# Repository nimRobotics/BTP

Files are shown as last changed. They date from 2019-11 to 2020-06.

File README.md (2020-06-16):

# :warning: [Deprecated for public use]

Please check <https://nimrobotics.github.io/OpenKDM/>.

# Introduction

This work titled as "Design and Fabrication of Experiment for Dynamic Analysis of Mechanisms " has been undertaken jointly by [Aakash Yadav](http://nimrobotics.github.io/) and Akhil Akunuru under the guidance of [Prof. Sriram Sundar](https://iittp.ac.in/dr-sriram-sundar).

|website| GitHub |
|--|--|
| [https://nimrobotics.github.io/BTP/](https://nimrobotics.github.io/BTP/) | [https://github.com/nimRobotics/BTP](https://github.com/nimRobotics/BTP) |

## Motivation and objective

The study of the *"Kinematics and Dynamics of Machinery" (IITT course code: ME2206)* lies at the very core of a mechanical engineering
background. Although, little has changed in the way the subject is presented, our methodology brings the subject alive and current. We
present the design and fabrication of a novel experimental setup for carrying out static, kinematic and dynamic analysis of three different
mechanisms in a single setup (Figure <a href="#cad_ful" data-reference-type="ref" data-reference="cad_ful">1</a>). The mechanism is designed to be configurable to three different types of mechanisms namely - double crank, slider crank and a six bar mechanism depending on the use case as shown in Figure <a href="#cad_all" data-reference-type="ref" data-reference="cad_all">2</a>. The mechanism has retrofitted parts (different link lengths and sliders) to facilitate multiple experiments in the same setup.

The learner gets to "play" with the mechanism parameters and immediately understand their effects. This will enhance one’s grasp of the concepts
and the development of analytical skills. Hence greatly supplementing and reinforcing the theoretical understanding of the undergraduate
students taking the course.

<figure align="center">
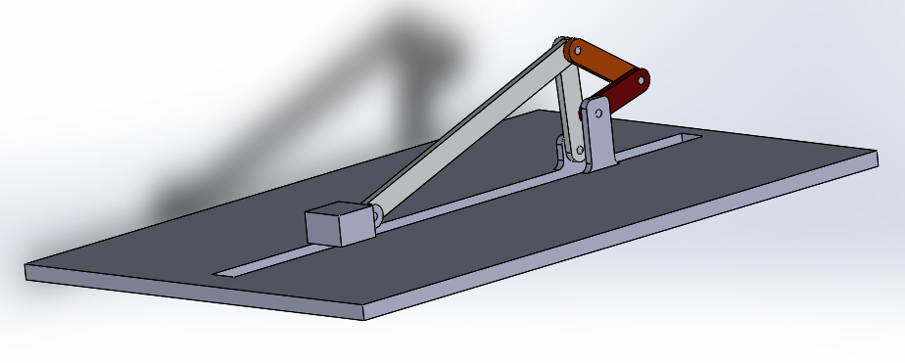
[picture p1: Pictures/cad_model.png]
<figcaption>1. CAD model of the mechanism</figcaption>
</figure>

<figure align="center">
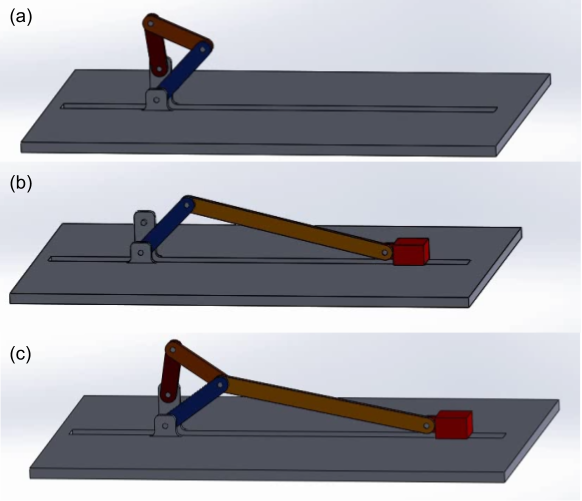
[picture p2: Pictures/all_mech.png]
<figcaption>2. Three possible configurations of the mechanism: (a) Four bar, (b) Slider crank and (c) Six bar</figcaption>
</figure>

## Present method(s) and challenges

In the present scenario finding standard mechanisms integrated with different sensor measurements and data acquisition is hard to find.
Almost all the mechanisms that are available off-the-shelf do not have any data measurement capability and thus can only be used for
demonstrations purpose and not as an experimental setup. 

In chapter 2 we present thoroughly all the methodologies used in designing and modeling the mechanisms. This includes both the analysis
carried out by analytical as well as numerical methods. In the chapter that follows we bring out the various design considerations that have to
be taken into account while manufacturing the product. The final two sections present the result(s) and the conclusion(s).

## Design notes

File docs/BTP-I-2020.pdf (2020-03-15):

## Department of Mechanical Engineering Indian Institute of Technology Tirupati

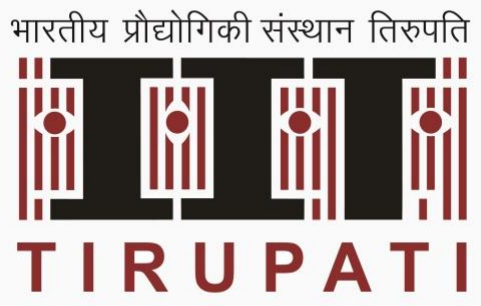
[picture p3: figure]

# B. Tech Final Year Project Presentation

## DESIGN AND FABRICATION OF EXPERIMENT FOR DYNAMIC ANALYSIS OF MECHANISMS

### 1. Aakash (ME16B001) 2. A. Akhil (ME16B003)

Supervised by
1. Dr. Sriram Sundar, Assistant Prof of ME

Date: 11-Mar-2020

## Objectives and Motivation

Dept. of
Mechanical
Engineering
B. Tech Final
Year Project
Presentation
- Introduction - Design and fabrication of experimental setup for static, kinematic and dynamic analysis of mechanisms with retrofitted parts.
- Motivation - The experiment will supplement and reinforce the theoretical understanding of the undergraduate students taking the ME2206 (KDM) course.

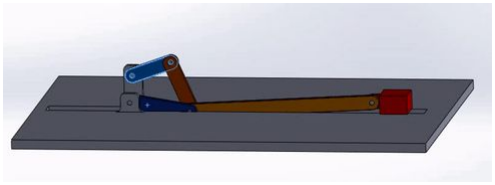
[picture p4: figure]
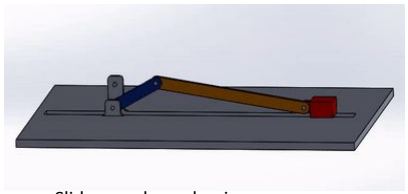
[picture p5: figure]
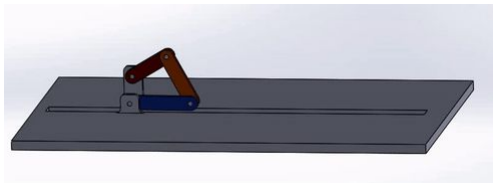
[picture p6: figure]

Four bar mechanism | Slider crank mechanism

Six bar mechanism

## Experiment plan

Aim:
1. To find the slider velocity and acceleration for six bar mechanism and slider crank mechanism
2. To find angular velocity and angular acceleration of all links in double crank mechanism.

Methodology and Results:
- This experimental setup will store the data of all parameters for each angular position.
- Students can select the angular position in the experimental setup to get the stored data display.
- Students need to solve theoretically for any particular angular position of mechanism.
- Students can compare theoretical results with practical results.

Engineering
Presentation

## Manufacturing plan

Engineering
Presentation

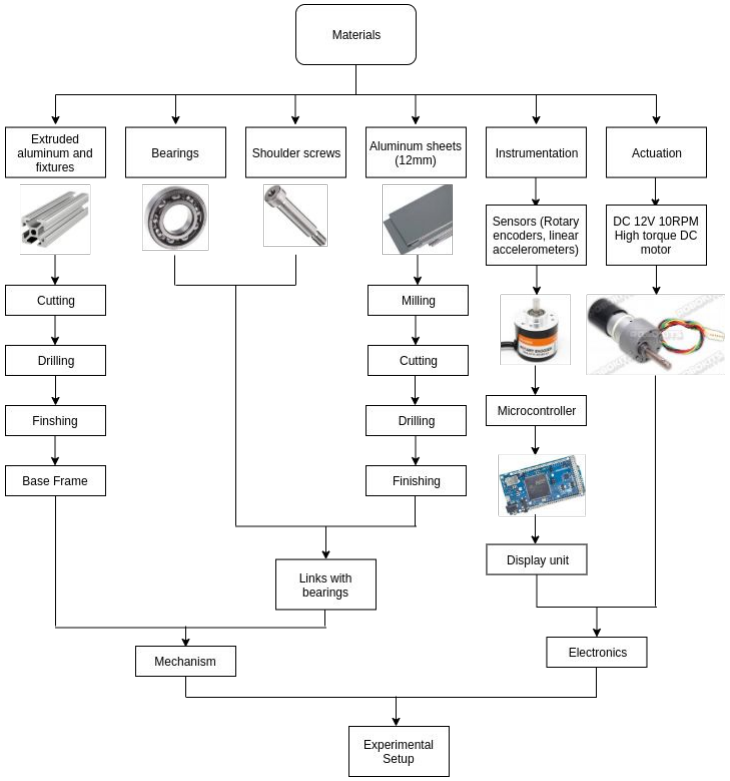
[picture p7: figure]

Sources: Bearing(SKF), Extruded Aluminum(indiamart.com), Shoulder screw(indiamart.com), AL sheets (indiamart.com)

## Updated CAD Design

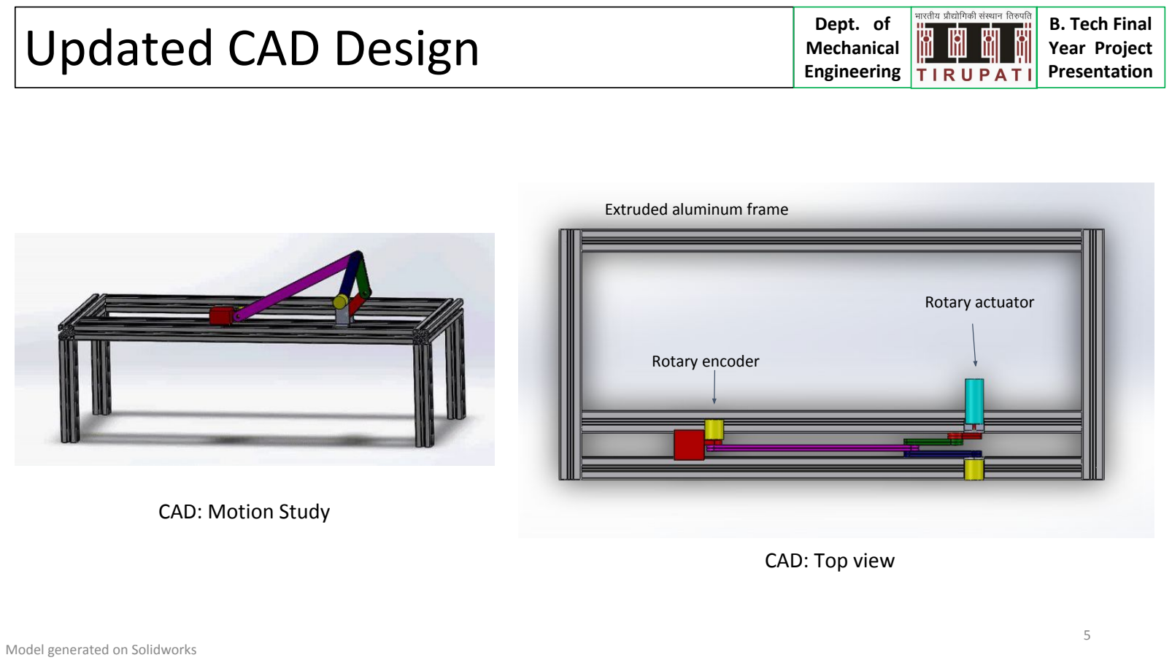
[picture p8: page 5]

Engineering
Presentation

CAD: Motion Study

CAD: Top view

Rotary actuator

Extruded aluminum frame

Rotary encoder

Model generated on Solidworks

## Raw materials

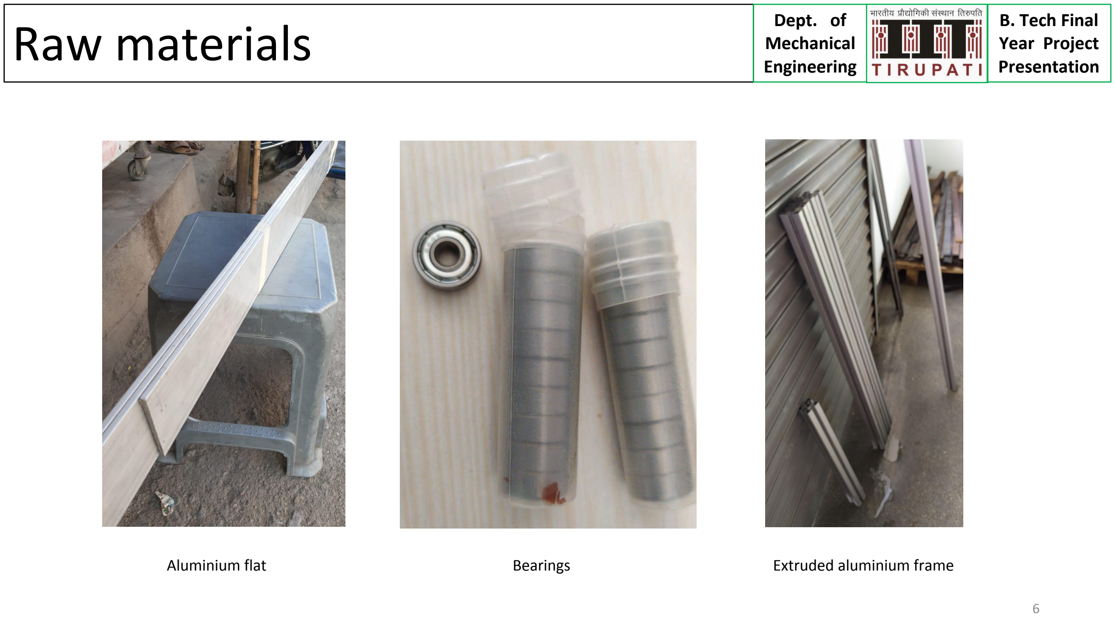
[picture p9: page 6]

Engineering
Presentation
Aluminium flat | Bearings | Extruded aluminium frame

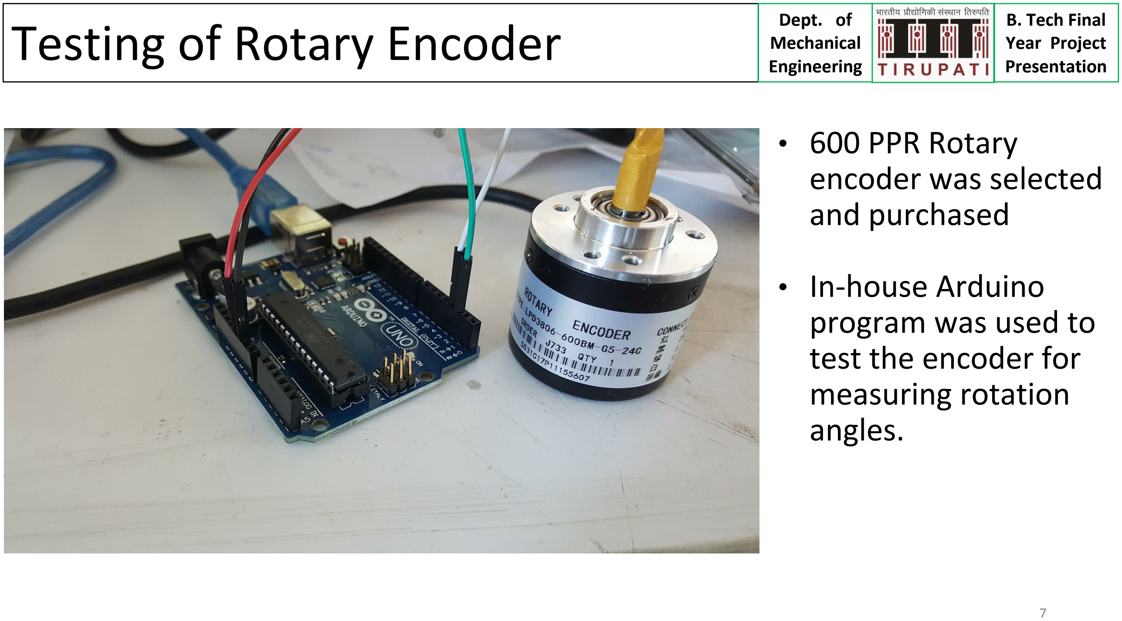
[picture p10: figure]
Testing of Rotary Encoder; Engineering; Presentation; • 600 PPR Rotary encoder was selected and purchased; • In-house Arduino program was used to test the encoder for measuring rotation angles.

## Actuator selection

Engineering
Presentation

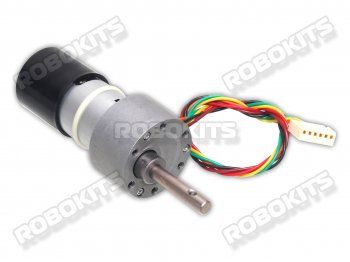
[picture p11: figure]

DC 12V 10 rpm high torque
quad encoder motor

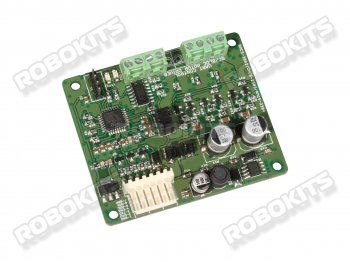
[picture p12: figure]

DC servo driver

Image source: Robokits India

## Fabrication

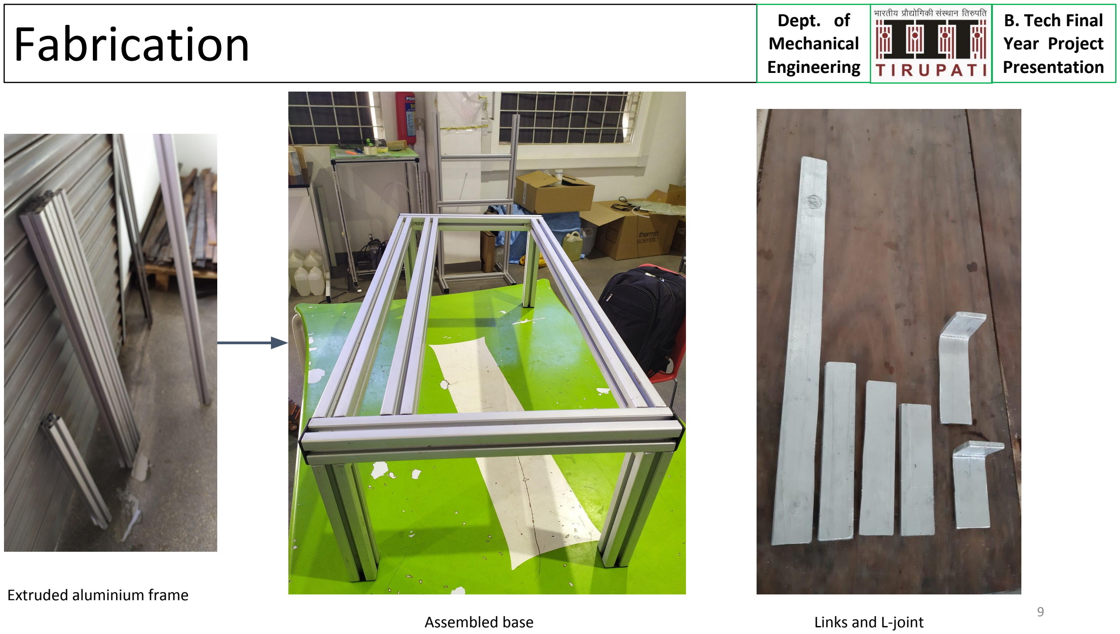
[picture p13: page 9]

Engineering
Presentation

Extruded aluminium frame

Assembled base | Links and L-joint

## Conclusions

- Full fledged CAD model of the mechanism was created considering all the manufacturing challenges (Design for manufacturing).
- All the required raw material were procured
- Rotary encoders were tested for angle measurement using Arduino.
- The base frame has been assembled while manufacturing and assembly of the links is in process.

Engineering
Presentation

## Future Work

Engineering
Presentation

Documentation

- Creation of
experiment
manual and
documentation.

Testing
(10th April)
- Experimentation,
testing and
validation.
- Design changes if
required

Fabrication
(31st March)
- Fabrication and
assembly of
links.
- Integration of
encoders and
other
electronics

## References

1. A. Ghosh and A. K. Mallik, Theory of mechanisms and machines. Affiliated East-West Press Private Limited, 2002.
2. R. L. Norton, Kinematics and dynamics of machinery. McGraw-Hill Higher Education, 2011.
3. J. J. Uicker, G. R. Pennock, J. E. Shigley, et al., Theory of machines and mechanisms, volume 1. Oxford University Press New York, NY, 2011.

Engineering
Presentation

## END

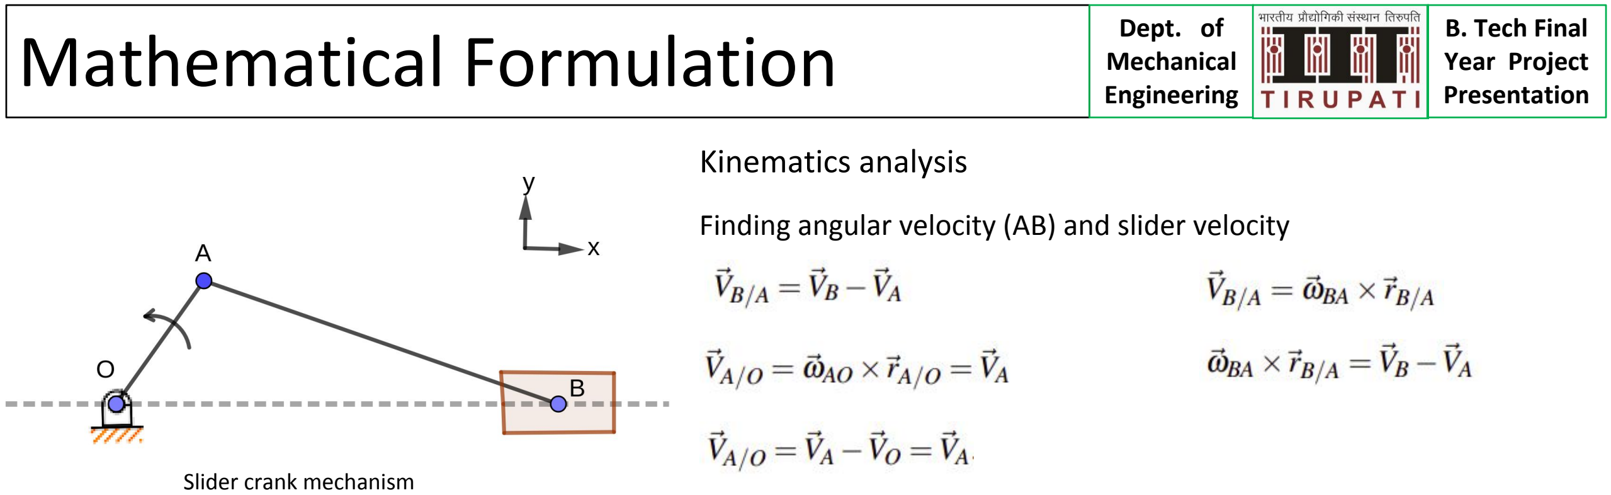
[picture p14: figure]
Mathematical Formulation; Engineering; Presentation; Kinematics analysis; Slider crank mechanism

Note: there may be missing steps and common notations for the sake of brevity. Refer to report for completeness.

Finding angular velocity (AB) and slider velocity

Finding angular acceleration (AB) and slider acceleration

## Mathematical Formulation

Engineering
Presentation

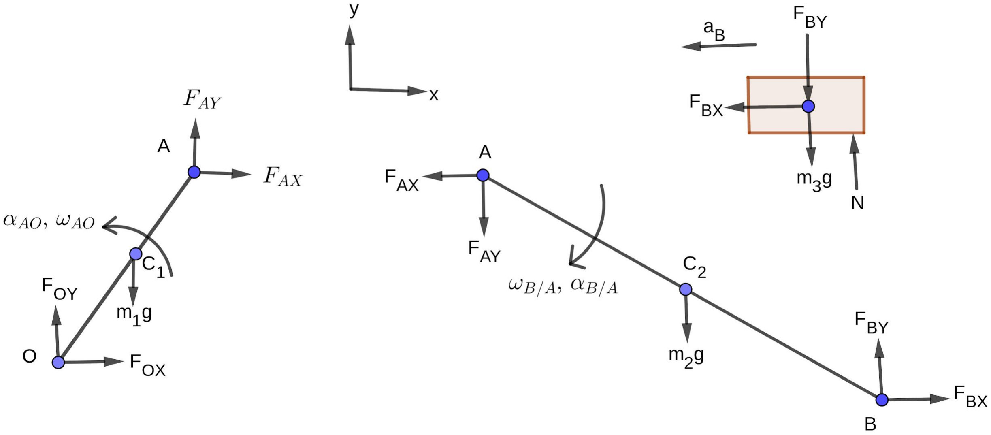
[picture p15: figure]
Slider crank mechanism

Dynamic analysis

Note: there may be missing steps and common notations for the sake of brevity. Refer to report for completeness.

Force balance for slider

Force and torque balance for link OA

Force and torque balance for link AB

Kinematic Analysis | Dept. of Engineering

Presentation
- By using Geogebra, we obtained preliminary link lengths and slider velocity profile.
- Analysed the velocity profile by changing link lengths.

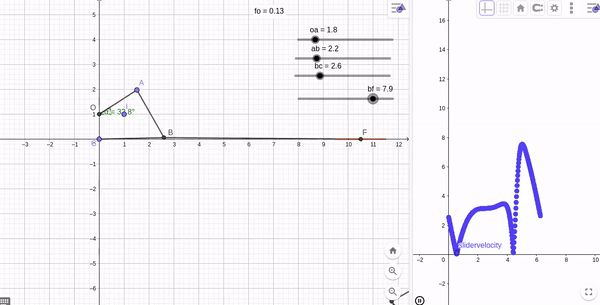
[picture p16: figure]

## Design for constant velocity

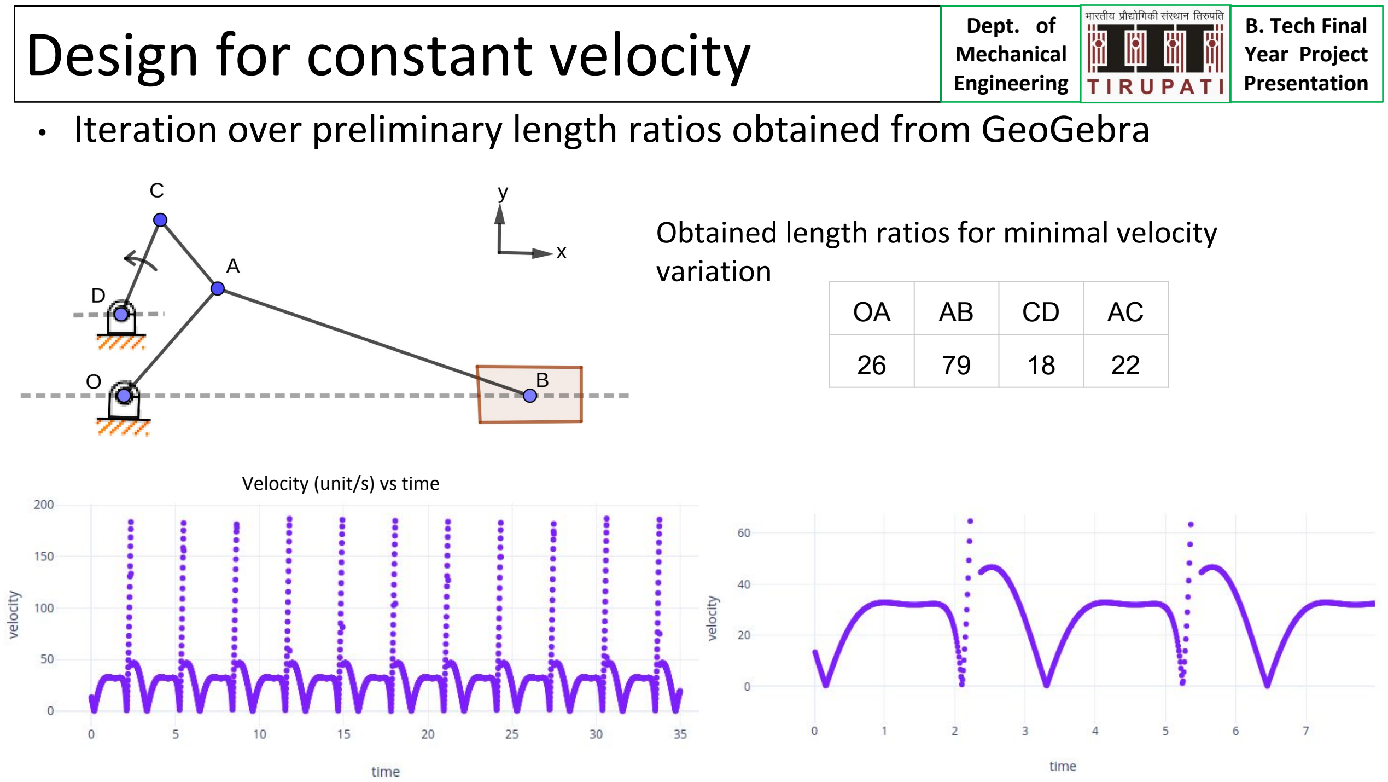
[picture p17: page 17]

- Iteration over preliminary length ratios obtained from GeoGebra

Engineering
Presentation
OA | AB | CD | AC
26 | 79 | 18 | 22

Obtained length ratios for minimal velocity variation

Velocity (unit/s) vs time

Dynamic Analysis | Dept. of

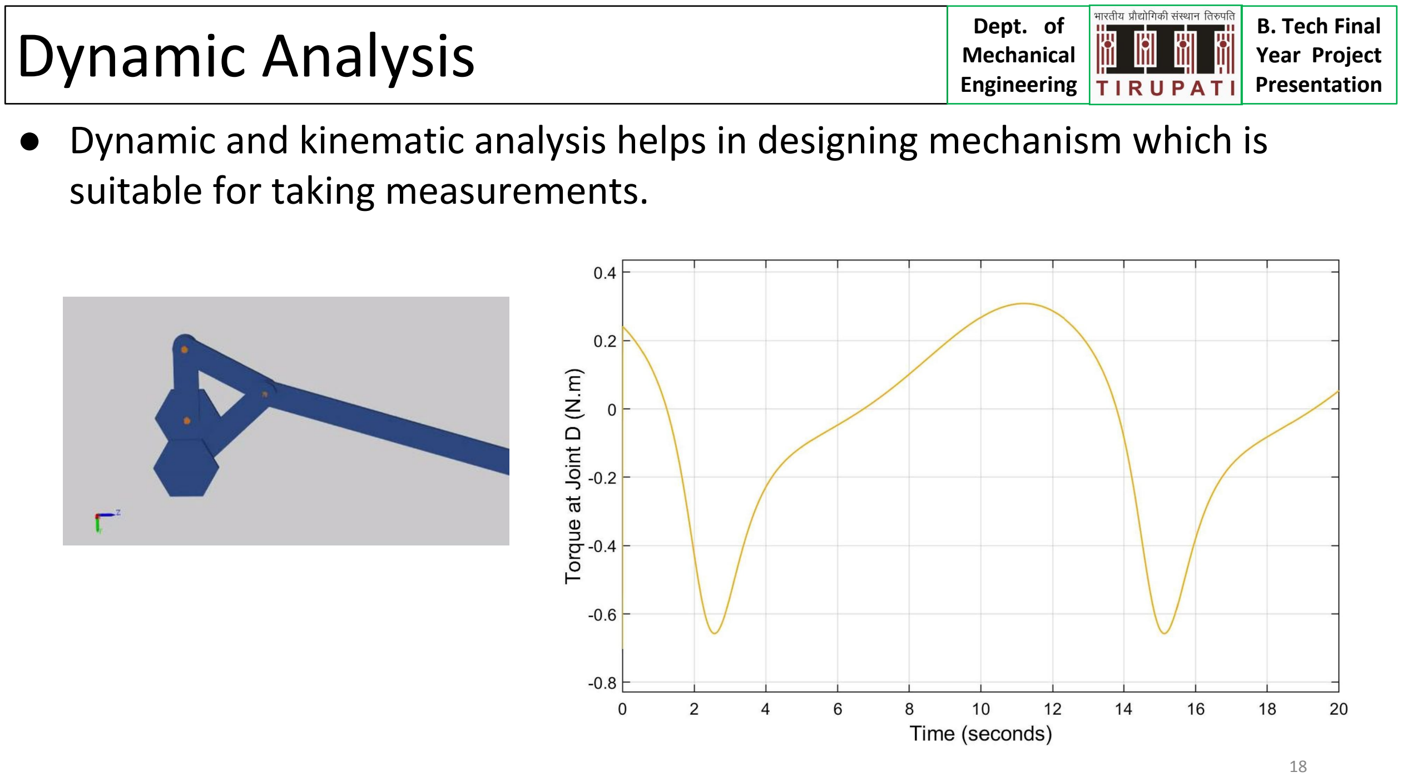
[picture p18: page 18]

Engineering
Presentation
- Dynamic and kinematic analysis helps in designing mechanism which is suitable for taking measurements.

## Results

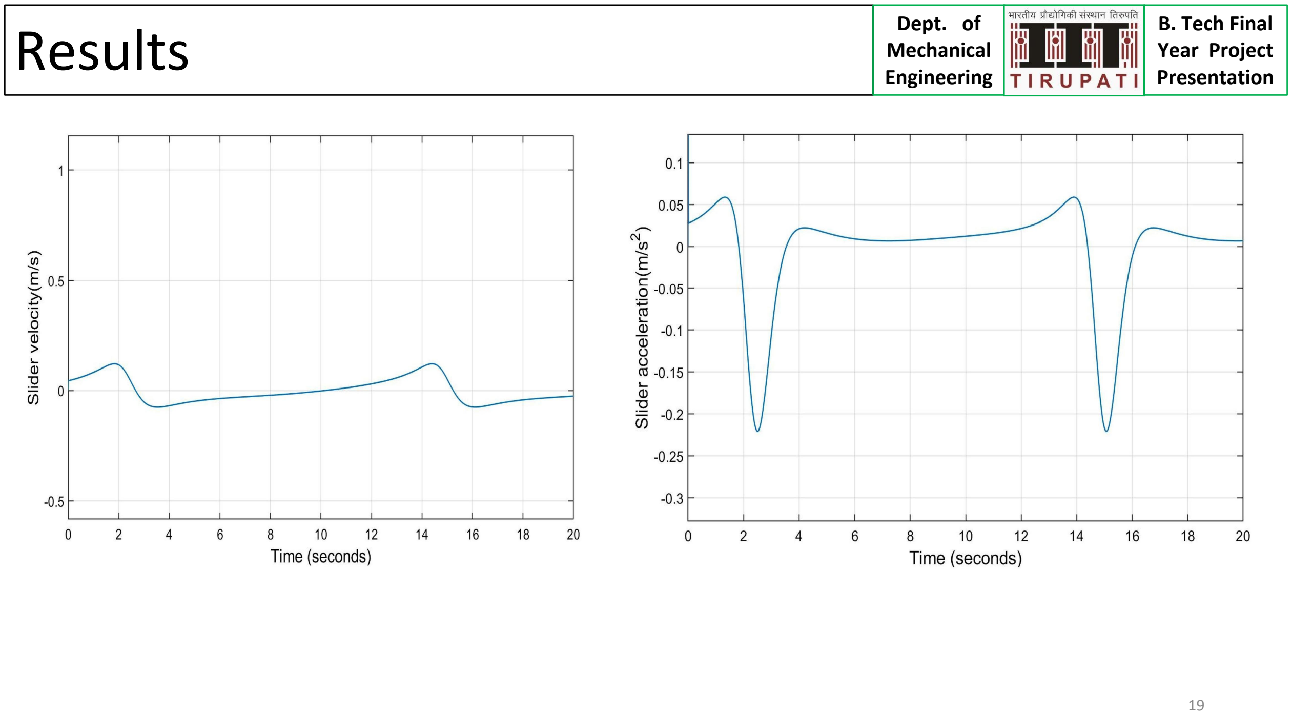
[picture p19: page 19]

Engineering
Presentation

## 3D Model

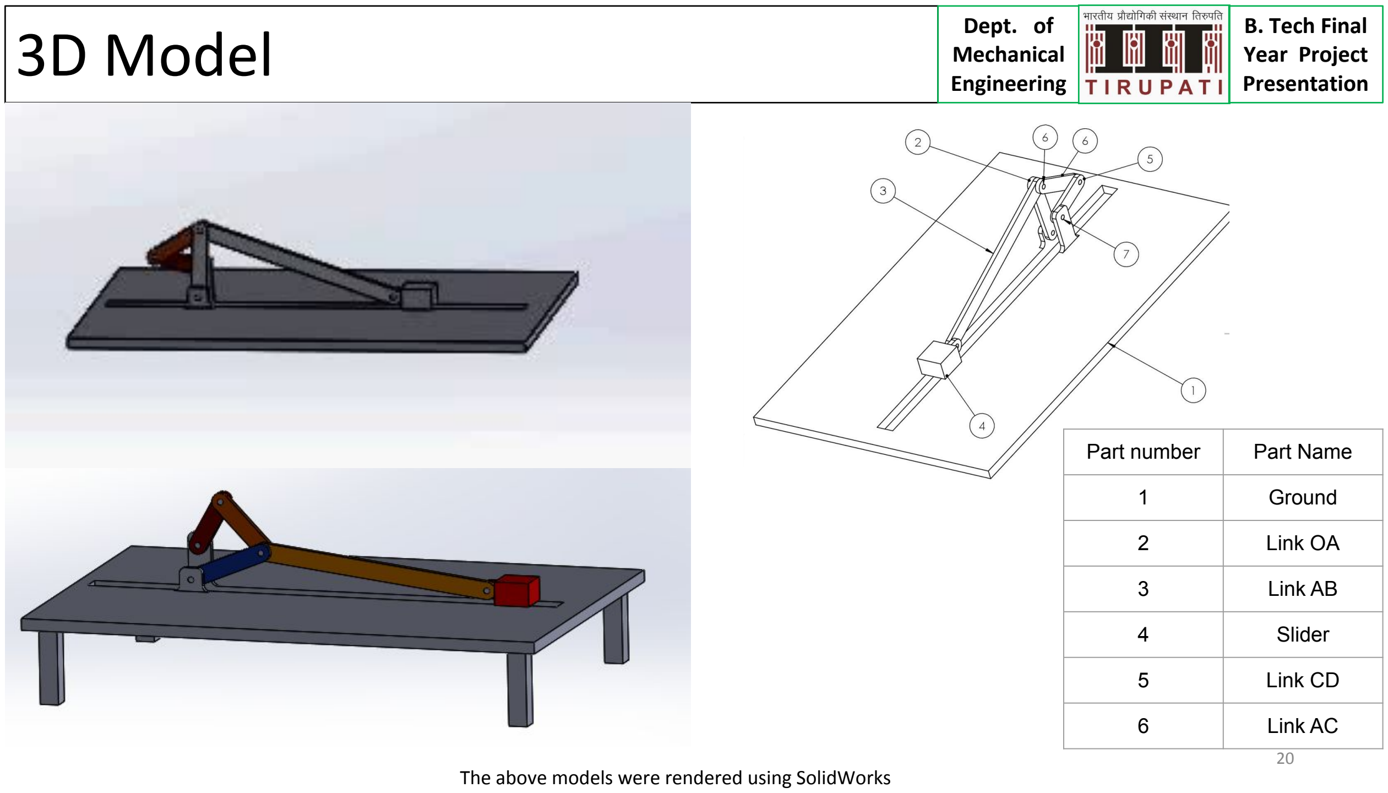
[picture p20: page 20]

Engineering
Presentation
Part number | Part Name
1 | Ground
2 | Link OA
3 | Link AB
4 | Slider
5 | Link CD
6 | Link AC

The above models were rendered using SolidWorks

## Sensor selection

Based on the results obtained from kinematic and dynamic analysis using MathWorks Simscape, we selected the required sensors.

- 2-Phase Incremental Optical Rotary Encoder to detect angular velocity and angular acceleration of links
- 3-Axis Accelerometer is to detect linear acceleration and linear velocity of slider.

Engineering
Presentation

Source: robu.in

Source: amazon.in

## Cost Analysis

Engineering
Presentation
No | Name | Unit cost in INR | Quantity | Cost in INR
1 | Bearing | 50 | 20 | 1000
2 | Shoulder screw | 20 | 6 | 120
3 | Aluminum (for links and slider) | 200 per kg | 15kg | 3000
4 | Extruded Aluminum | 400 per m | 5 | 2000
5 | Actuator | - | - | -
6 | Rotary Encoder | 2000 | 3 | 6000
7 | Linear Accelerometer (8kHz) | 200 | 1 | 200
8 | Display | 1000 | 1 | 1000
9 | Other Electronics and miscellaneous | | | 5000
10 | Slotted weights, pulley | 2000 | 1 | 2000
| Grand Total | | | 20,320/-

Note: tentative, minor changes may occur.

## Conclusions

- The complete analysis of the mechanism(s) was performed using applicable method and software.
- 3D CAD model of the mechanism was created to facilitate better visualisation.
- Various design considerations were addressed and manufacturing workflow and plan were accomplished as a prerequisite to manufacturing.
- BoM was prepared and materials acquisition from the vendor is in process.

Engineering
Presentation

## Future Work

Engineering
Presentation

Fabrication

- Fabrication and
assembling of
links.
- Experimentation,
testing and
validation.

Final Design

- Final prototype
model consisting
of links, bearings,
motors, sensors,
etc.

Actuator selection

- Need to find the
best actuator
with its control
system.

## References

1. MATLAB version 9.3.0.713579 (R2017b). The Mathworks, Inc., Natick, Massachusetts, 2017.
2. A. Ghosh and A. K. Mallik, Theory of mechanisms and machines. Affiliated East-West Press Private Limited, 2002.
3. M. Hohenwarter, M. Borcherds, G. Ancsin, B. Bencze, M. Blossier, A. Delobelle, C. Denizet, J. Éliás, A. Fekete, L. Gál, Z. Konecný ˇ , Z. Kovács, S. Lizelfelner, B. Parisse, and G. Sturr (2013). GeoGebra 4.4. http://www.geogebra.org.
4. R. L. Norton, Kinematics and dynamics of machinery. McGraw-Hill Higher Education, 2011.
5. Python Core Team (2018). Python: A dynamic, open source programming language. Python Software Foundation. URL https://www.python.org/.
6. J. J. Uicker, G. R. Pennock, J. E. Shigley, et al., Theory of machines and mechanisms, volume 1. Oxford University Press New York, NY, 2011.

Engineering
Presentation

## Acknowledgements

Thanks to all those who helped us during the course of our B.Tech. project at IIT Tirupati. We are thankful to and fortunate enough to get constant encouragement, support and guidance from Dr. Sriram Sundar of Mechanical Engineering Department which helped us in successfully completing first phase of our project work. We would also like to extend our sincere esteems to all staff in laboratory for their timely support.

To our families, thank you for encouraging us in all of our pursuits and inspiring us to follow our dreams. We are especially grateful to our parents, who supported us emotionally and financially.

Engineering
Presentation

## END

## Supplementary material

## Updates

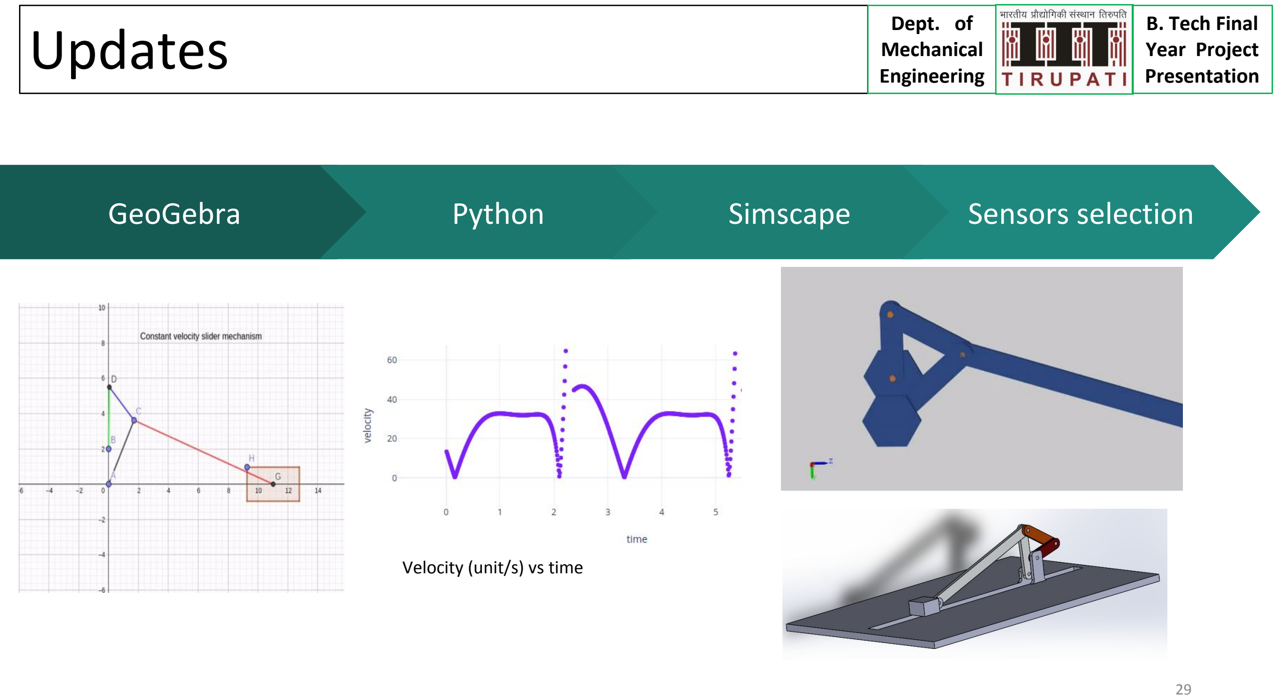
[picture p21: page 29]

Engineering
Presentation
GeoGebra | Python | Simscape | Sensors selection

Velocity (unit/s) vs time

## Introduction and Objectives

- To design and fabricate an experimental setup for static, kinematic and dynamic analysis of mechanism.
- The setup will have retrofitted parts in order to let the student carry out multiple experiments in the same setup.
- The experiment will supplement and reinforce the theoretical understanding of the undergraduate students taking the ME2206(KDM) by providing them the opportunity to match the analytical results with the actual experimental results.

Engineering
Presentation

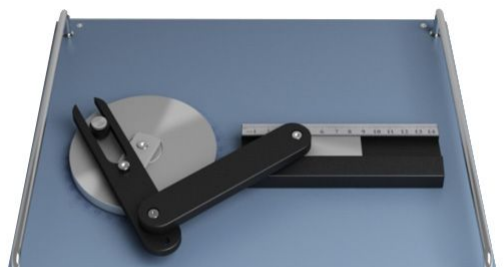
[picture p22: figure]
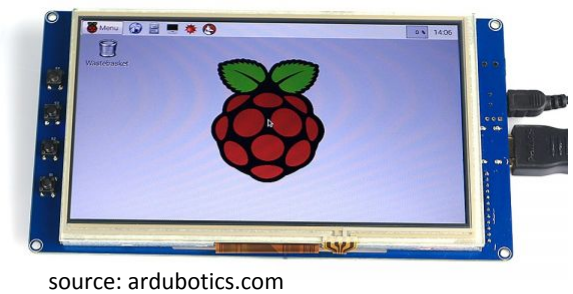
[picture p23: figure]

source: sun labtech source: ardubotics.com

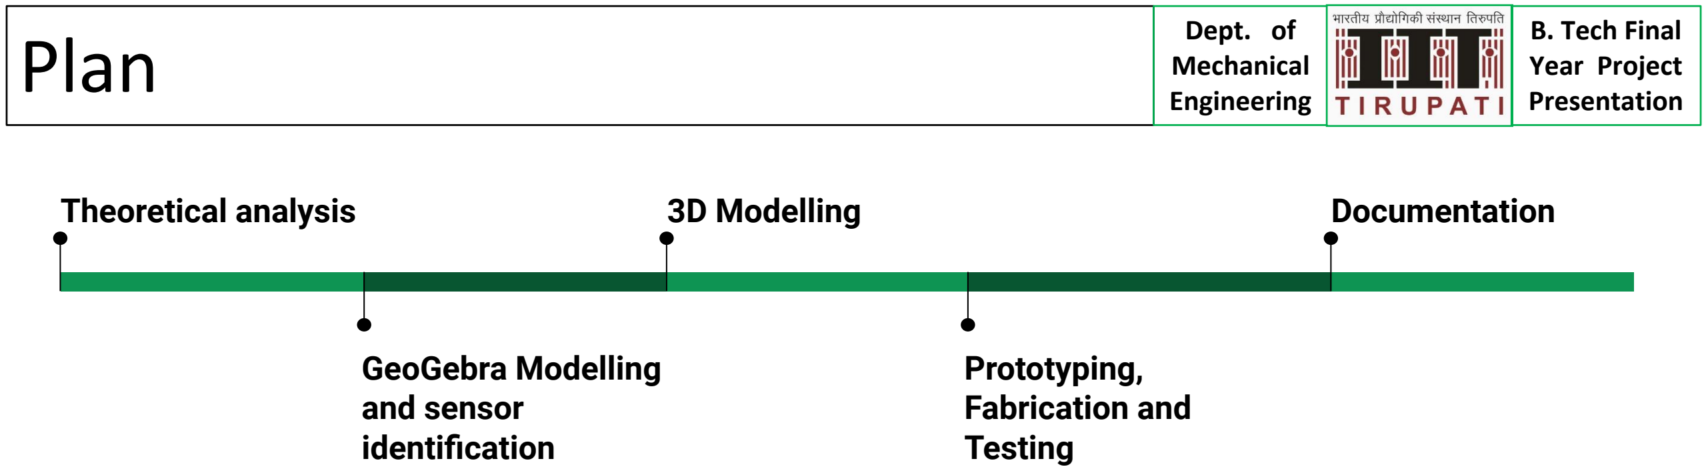
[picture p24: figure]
Plan; Engineering; Presentation; 3D Modelling; Prototyping, Fabrication and Testing; Theoretical analysis; GeoGebra Modelling and sensor identification; Documentation

Estimated budget : INR 25,000.00 - 30,000.00

Probable sensors for instrumentation: Rotary encoders, Ultrasonic range sensors, linear accelerometers, strain gauges

## Literature Review

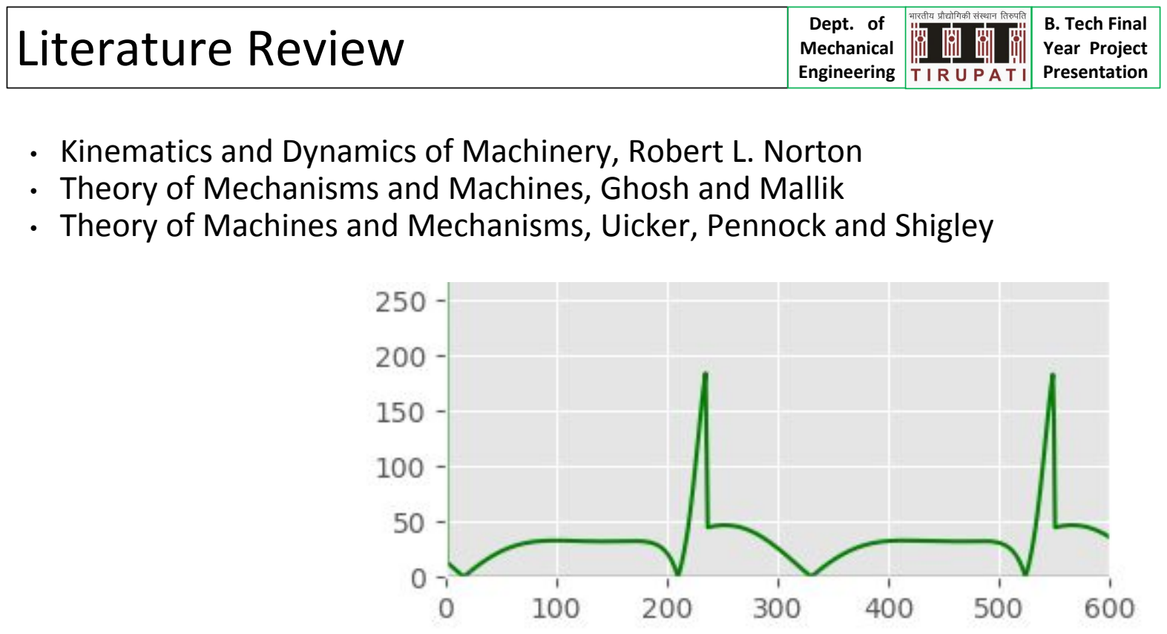
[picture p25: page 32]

- Kinematics and Dynamics of Machinery, Robert L. Norton
- Theory of Mechanisms and Machines, Ghosh and Mallik
- Theory of Machines and Mechanisms, Uicker, Pennock and Shigley

Engineering
Presentation

## Mechanism

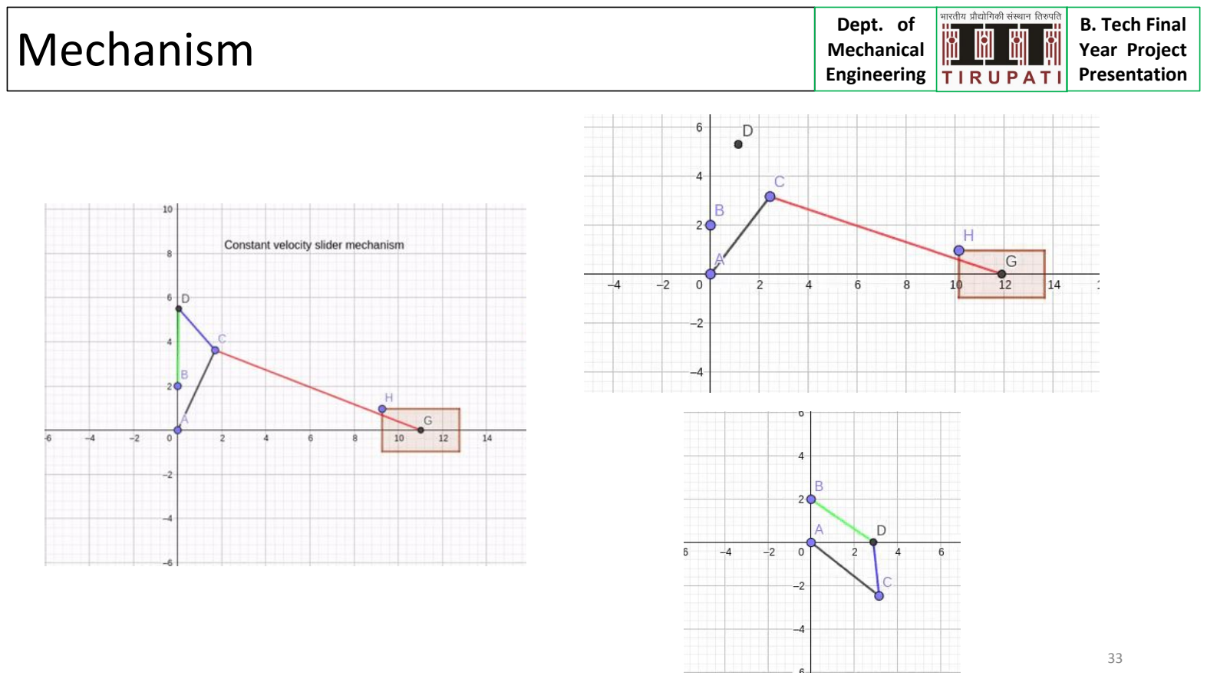
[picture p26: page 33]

Engineering
Presentation

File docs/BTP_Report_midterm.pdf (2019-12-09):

## Design and Fabrication of Experiment for Dynamic

## Analysis of Mechanisms

submitted in partial fulfilment of the requirements

for the degree of

BACHELOR OF TECHNOLOGY

in

MECHANICAL ENGINEERING

by

### AAKASH ME16B001

### A. AKHIL ME16B003

### Supervisor(s)

### Dr. Sriram Sundar

### DEPARTMENT OF MECHANICAL ENGINEERING

### INDIAN INSTITUTE OF TECHNOLOGY TIRUPATI

### December 2019

## DECLARATION

We declare that this written submission represents our ideas in our own words

and where others’ ideas or words have been included, we have adequately cited and

referenced the original sources. We also declare that we have adhered to all principles of

academic honesty and integrity and have not misrepresented or fabricated or falsified any

idea/data/fact/source in our submission. We understand that any violation of the above

will be cause for disciplinary action by the Institute and can also evoke penal action from

the sources which have thus not been properly cited or from whom proper permission

has not been taken when needed.

Place: Tirupati
Date: 06-12-2019

Signature
Aakash
ME16B001

Place: Tirupati
Date: 06-12-2019

Signature
A. Akhil
ME16B003

## BONA FIDE CERTIFICATE

This is to certify that the thesis titled Design and Fabrication of Experiment for

Dynamic Analysis of Mechanisms, submitted by Aakash and A. Akhil, to the Indian

Institute of Technology, Tirupati, for the award of the degree of Bachelor of Technology,

is a bona fide record of the research work done by them under my supervision. The

contents of this thesis, in full or in parts, have not been submitted to any other Institute

or University for the award of any degree or diploma.

Place: Tirupati
Date: 08-12-2019

Dr. Sriram Sundar
Guide
Assistant Professor
Department of Mechanical
Engineering
IIT Tirupati - 517501

## ACKNOWLEDGEMENTS

Thanks to all those who helped us during the course of our B.Tech. project at IIT Tirupati.

We are thankful to and fortunate enough to get constant encouragement, support and

guidance from Dr. Sriram Sundar of Mechanical Engineering Department which helped

us in successfully completing first phase of our project work. We would also like to

extend our sincere esteems to all staff in laboratory for their timely support.

To our families, thank you for encouraging us in all of our pursuits and inspiring us

to follow our dreams. We are especially grateful to our parents, who supported us

emotionally and financially.

i

## ABSTRACT

KEYWORDS: Slider crank mechanism; Four bar mechanism; Six-bar mechanism;

Dynamic analysis; Kinematic analysis; Simulation.

This report explains the detailed process of design and analysis of an experimental

setup, which consists of a 3-in-1 mechanism. The setup is designed to perform static,

kinematic and dynamic analysis of mechanisms. The design and analysis were performed

analytically and numerically by using various commercial software’s. The results thus

obtained were used to determine the link geometry of the mechanism and in selecting

the suitable sensors which in turn will be used for fabrication and instrumentation.

ii

## TABLE OF CONTENTS

ACKNOWLEDGEMENTS | i
ABSTRACT | ii
LIST OF FIGURES | v
LIST OF TABLES | vi
ABBREVIATIONS | vii
NOTATION | viii
1 INTRODUCTION | 1
2 ANALYSIS OF MECHANISMS | 3
3 MANUFACTURING | 15
4 RESULTS | 17
5 CONCLUSION AND FUTURE WORK | 19

iii

A CODE LISTING | 20

## LIST OF FIGURES

1.1 CAD model of the mechanism | | 1

1.2 Three possible configurations of the mechanism: (a) Four bar, (b) Slider
crank and (c) Six bar | | 2
2.1 Slider crank mechanism | | 4
2.2 Four bar mechanism | | 5
2.3 Six bar mechanism | | 6

2.4 Snapshot from GeoGebra showing the mechanism (left) and the velocity
profile (right) | | 8
2.5 Output window from Python for kinematic simulation | | 9
2.6 Free Body Diagram for Slider Crank Mechanism | | 10
2.7 Free Body Diagram for four-bar mechanism | | 12
2.8 Free Body Diagram for six-bar mechanism | | 13
2.9 CAD model in MATLAB Simscape | | 13
2.10 Results obtained from Simscape | | 14
3.1 3D Model of the experiment on (table) | | 15
3.2 Flowchart showing manufacturing | | 16
4.1 Slider Velocity | | 17
4.2 Slider acceleration | | 18

v

## LIST OF TABLES

2.1 GeoGebra results | | 9
4.1 Final link lengths | | 17

vi

## ABBREVIATIONS

The following list describes the significance of various abbreviations and acronyms used

throughout the report.

KDM | Kinematics and Dynamics of Machinery
PMSM | Permanent Magnet Synchronous Motor
CAD | Computer Aided Design
CSV | Comma Seperated Values
FBD | Free Body Diagram

vii

## NOTATION

The following notations are used throughout the report.

~rA/B | Position vector of point A with respect to point B, m
ωAB | Angular velocity of link AB, rad
| s
~VA/B | Velocity vector of point A with respect to point B, m
| s
~aA/B | Acceleration vector of point A with respect to point B,

m
s

2
αAB | Angular acceleration of link AB, rad
| s
| 2

viii

## CHAPTER 1

## INTRODUCTION

## 1.1 Motivation and objective

The study of the "Kinematics and Dynamics of Machinery" (IITT course code: ME2206)

lies at the very core of a mechanical engineering background. Although, little has

changed in the way the subject is presented, our methodology brings the subject alive and

current. We present the design and fabrication of a novel experimental setup for carrying

out static, kinematic and dynamic analysis of three different mechanisms in a single

setup (Figure 1.1). The mechanism is designed to be configurable to three different types

of mechanisms namely - double crank, slider crank and a six bar mechanism depending

on the use case as shown in Figure 1.2. The mechanism has retrofitted parts (different

link lengths and sliders) to facilitate multiple experiments in the same setup.

The learner gets to "play" with the mechanism parameters and immediately understand

their effects. This will enhance one’s grasp of the concepts and the development of ana-

lytical skills. Hence greatly supplementing and reinforcing the theoretical understanding

of the undergraduate students taking the course.


Figure 1.1: CAD model of the mechanism

## 1.2 Present method(s) and challenges

In the present scenario finding standard mechanisms integrated with different sensor

measurement and data acquisition is hard to find. Almost all the mechanisms that are


Figure 1.2: Three possible configurations of the mechanism: (a) Four bar, (b) Slider crank and (c) Six bar

available off-the-shelf do not have any data measurement capability and thus can only be

used for demonstrations purpose and not as an experimental setup.

In chapter 2 we present thoroughly all the methodologies used in designing and modelling

the mechanisms. This includes both the analysis carried out by analytical as well

as numerical methods. In the chapter that follows we bring out the various design

considerations that has to be taken into account while manufacturing the product. The

final two sections present the result(s) and the conclusion(s).

## CHAPTER 2

## ANALYSIS OF MECHANISMS

## 2.1 Kinematic analysis

This section presents the methodology employed in order to simulate the kinematics of

the various mechanisms. In order to carry out the preliminary analysis of the mechanism,

GeoGebra an interactive math and geometry software was used. This provided the coarse

link lengths required for having the least deviant constant velocity mechanism as shown

in Figure 2.4. Once the coarse link lengths were obtained, we developed an in-house

Python code that can do iterations on the link lengths so as to minimise any fluctuations

in the constant velocity mechanism. The visual output of the Python simulation can be

seen in Figure 2.5 while rest of the simulation data is store in a CSV file.

### 2.1.1 Mathematical formulation

This section brings out the equations of motion associated with the three different

mechanisms (Norton, 2011; Uicker et al., 2011). These equations are used to carry out

the kinematic and dynamics method theoretically, which then in turn be compared with

the numerical solutions obtained by other simulation tools.

Slider crank mechanism

The equations of motion pertaining to the slider crank mechanism (Figure 2.1) are

presented in this subsection.

~VB/A =~VB −~VA | (2.1)

For link OA we have

~VA/O = ω~ AO ×~rA/O =~VA | (2.2)


Figure 2.1: Slider crank mechanism

Since ’O’ is ground link we have ~VO = 0 =⇒ ~VA/O =~VA −~VO =~VA. As point B lies on

the slider and is moving leftwards it will have velocity along the negative x-direction i.e.

~VB = −VB
ˆi; because ω~ AO = ωAOˆk. For link AB we have
~VB/A = ω~ BA ×~rB/A | (2.3)

Substituting equation 2.3 in equation 2.1 we obtain

ω~ BA ×~rB/A =~VB −~VA | (2.4)

Using equation 2.4 we can find ωBA and VB. For finding the accelerations we can write

~aA/O =~aA =~a

t
A +~a

n
A

(2.5a)

~a

t
A = α~A/O ×rA~/O | (2.5b)

~a

n
A = ω~AO ×ω~AO ×rA~/O | (2.5c)

where, ~a

t
A

and ~a

n
A

denote the tangential and normal acceleration of point A. As point B

lies on the slider, we have ~aB = aB

ˆi.

~aB/A =~a

t
B/A +~a

n
B/A =~aB −~aA | (2.6)


Figure 2.2: Four bar mechanism

Using the above equation we can find αBA and ~aB.

Four bar mechanism (with four revolute joints)

This subsection lists the mathematical equations pertaining to the four bar mechanism

(Figure 2.2).

~VA/O = ω~ AO ×~rA/O =~VA | (2.7a)
~VC/D = ω~ CD ×~rC/D =~VC | (2.7b)
~VA/C = ω~ AC ×~rA/C =~VA −~VC = ω~ AO ×~rA/O −ω~ CD ×~rC/D | (2.8)

Using the above equation we can find ωCD and ωAC.

~aA/O =~aA =~a

t
A +~a

n
A

(2.9a)


Figure 2.3: Six bar mechanism

~aC/D =~aC =~a

t
C +~a

n
C

(2.9b)

~aA/C =~a

t
A/C +~a

n
A/C =~aA −~aC | (2.10)

Here~a

t =~α ×~r and ~a

n = ω~ ×ω~ ×~r. Using the above equations we can find αAC and αCD

Six bar mechanism

This subsection presents the mathematical equations associated with the six bar mecha-

nism (Figure 2.3).

~VC/D = ω~ CD ×~rC/D =~VC | (2.11)
~VA/C = ω~ AC ×~rA/C =~VA −~VC = ω~ AO ×~rA/O −ω~ CD ×~rC/D | (2.12)

Using the above equation we can find ωOA and ωAC.

~VB/A =~VB −~VA | (2.13)

For link OA we have

~VA/O = ω~ AO ×~rA/O =~VA | (2.14)

Since ’O’ is ground link we have ~VO = 0 =⇒ ~VA/O =~VA −~VO =~VA. As point B lies on

the slider and is moving leftwards it will have velocity along the negative x-direction i.e.

~VB = −VB
ˆi; because ω~ AO = ωAOˆk. For link AB we have
~VB/A = ω~ BA ×~rB/A | (2.15)

Substituting equation 2.15 in equation 2.13 we obtain

ω~ BA ×~rB/A =~VB −~VA | (2.16)

Using equation 2.16 we can find ωBA and VB.

For finding the accelerations we can write

~aC/D =~aC =~a

t
C +~a

n
C

(2.17)

~aA/C =~a

t
A/C +~a

n
A/C =~aA −~aC | (2.18)

Here~a

t =~α ×~r and ~a

n = ω~ ×ω~ ×~r. Using the above equations we can find αAC and αOA

~aA/O =~aA =~a

t
A +~a

n
A

(2.19a)

~a

t
A = α~A/O ×rA~/O | (2.19b)

~a

n
A = ω~AO ×ω~AO ×rA~/O | (2.19c)

where, ~a

t
A

and ~a

n
A

denote the tangential and normal acceleration of point A. As point B

lies on the slider, we have ~aB = aB

ˆi.

~aB/A =~a

t
B/A +~a

n
B/A =~aB −~aA | (2.20)

Using the above equation we can find αBA and ~aB.

### 2.1.2 GeoGebra modelling

This subsection provides an insight into the preliminary analysis done by using off-the-

shelf software - GeoGebra for determining initial link lengths (Hohenwarter et al., 2013).

First the mechanism was created inside GeoGebra geometry with sliders for varying the

link lengths manually. Later the slider velocity was plotted by using graphical analysis

of the mechanism inside GeoGebra itself (as shown in Figure 2.4). In order to find the

required link lengths yielding constant velocity mechanism, each of the link lengths

were varied to get the constant velocity mechanism with least variation while keeping

the others fixed. The manual iterations are shown in Table 2.1.


Figure 2.4: Snapshot from GeoGebra showing the mechanism (left) and the velocity profile (right)

### 2.1.3 Python simulation

This section deals with further refining the preliminary links lengths which were obtained

from GeoGebra modelling. The initial lengths are fed to an in-house Python script (see

appendix) to get optimum link lengths for nearly constant slider velocity (Python Core

Team, 2018). The algorithm performs the iterations by varying each of the link by step

size of 0.1×unit length. It also stores the peak to valley distance for each of the obtained

velocity profiles which can be used to select the link lengths giving minimum velocity

variation for the constant velocity range. Figure 2.5 shows the mechanism animation as

OC | OA | AB | BC | BF | Mean slider velocity | Peak to valley of slider velocity | ω of crank
1 | 2 | 1.6 | 2 | 6 | 2.25 | 0.5 | 2
1 | 2 | 1.4 | 2 | 6 | 2.28 | 0.81 | 2
1 | 2 | 1.2 | 2 | 6 | 2.37 | 1.24 | 2
1 | 2 | 2 | 2 | 6 | 2.385 | 0.77 | 2
1 | 2.2 | 1.6 | 2 | 6 | 2.31 | 0.83 | 2
1 | 1.8 | 1.6 | 2 | 6 | 2.375 | 0.75 | 2
1 | 2 | 1.6 | 2.2 | 6 | 2.545 | 0.37 | 2
1 | 2 | 1.6 | 1.8 | 6 | 1.92 | 0.76 | 2
1 | 2 | 1.6 | 2.4 | 6 | 2.87 | 0.26 | 2
1 | 2 | 1.6 | 2.6 | 6 | 3.2 | 0.25 | 2
1 | 2 | 1.6 | 2.8 | 6 | 3.52 | 0.36 | 2
1 | 2 | 1.6 | 2.6 | 7 | 3.135 | 0.15 | 2
1 | 2 | 1.6 | 2.6 | 7.5 | 3.2 | 0.12 | 2
1 | 2 | 1.6 | 2.6 | 8 | 3.24 | 0.09 | 2
All lengths are in units, velocity are in units/s, angular velocity ω is in rad/s.

Table 2.1: GeoGebra results


Figure 2.5: Output window from Python for kinematic simulation

well as the velocity plot having a near constant velocity for an interval.


Figure 2.6: Free Body Diagram for Slider Crank Mechanism

## 2.2 Dynamic analysis

For performing the dynamic analysis of the mechanism we used MathWorks Simscape

Mechanical package. A 3D model was created in the package itself and analysed the

same for various forces, torques, acceleration and velocities by taking the material as

aluminium (Figure 2.9, ??). This analysis is necessary in order to ease the process of

selection of actuator, material and the sensor system.

### 2.2.1 Mathematical formulation

This subsection brings out the mathematical equations for performing dynamic analysis

of all the three possible mechanism (Ghosh and Mallik, 2002).

Slider crank mechanism

Force and Torque balance for link OA using Figure 2.6

FOX +FAX = 0 | (2.21a)
FOY +FAY = m1g | (2.21b)

IAO~αAO =~rC1O ×m1g(− ˆj) +~rA/O ×~FA | (2.21c)

where, ~FA = ~FAX ˆi+~FAY ˆj. Similarly for link AB we have

FAX = FBX | (2.22a)
FBY = FAY +m2g | (2.22b)
IBA~αB/A =~rC2/A ×m2g(− ˆj) +~rB/A ×~FB | (2.22c)

where, ~FB = ~FBX ˆi+~FBY ˆj.

Force balance for the slider

FBY +m3g = N | (2.23a)
m3aB = FBX | (2.23b)

Four bar mechanism (with four revolute joints)

Force and Torque balance for link OA using Figure 2.7

∑F~X = 0 | (2.24a)
∑F~Y = 0 | (2.24b)
∑~T = I1~αAO | (2.24c)

Force and Torque balance for link AC using Figure 2.7

∑F~X = 0 | (2.25a)
∑F~Y = 0 | (2.25b)


Figure 2.7: Free Body Diagram for four-bar mechanism

∑~T = I4~αAC | (2.25c)

Force and Torque balance for link CD using Figure 2.7

∑F~X = 0 | (2.26a)
∑F~Y = 0 | (2.26b)
∑~T = I5~αCD | (2.26c)

Six bar mechanism

Force and Torque balance for all links using Figure 2.8

∑F~X = 0,∑F~Y = 0,∑~T = I~α | (2.27)
FA1X +FA2X +FA4X = 0 | (2.28a)
FA1Y +FA2Y +FA4Y = 0 | (2.28b)


Figure 2.8: Free Body Diagram for six-bar mechanism

Force balance for Slider using Figure 2.8

FBY +m3g = N | (2.29a)
m3aB = FBX | (2.29b)

### 2.2.2 Using commercial software: MathWorks Simscape

This sections deals with the dynamic analysis of the mechanism using Mathworks

Simscape. A MathWorks Simscape model (Figure 2.9) was created based on the link

lengths that were obtained from the kinematic analysis.The link width is taken as 3cm

and link thickness as 1cm while taking aluminum as material for all links and slider.

(MAT, 2017)


Figure 2.9: CAD model in MATLAB Simscape


(a) Input torque
(b) Slider force

Figure 2.10: Results obtained from Simscape

## CHAPTER 3

## MANUFACTURING

### 3.0.1 Sensor selection

Based on the results of Kinematic, Dynamic analysis using MathWorks Simscape, We

selected 2-Phase Incremental Optical Rotary Encoder to detect angular velocity and

angular acceleration of links, 3-Axis Accelerometer is to detect linear acceleration and

linear velocity of slider.

2-Phase Incremental Optical Rotary Encoder has 600 Pulse Per Revolution (PPR).

3-Axis Accelerometer has range of −16g to 16g, with a sampling rate of 8kHz.

### 3.0.2 Manufacturing plan

This section focuses on the materials and fabrication processes that will be used for

carrying out the manufacturing in the second phase of the project. Figure 3.2 gives

complete insight on the various stages involved in manufacturing the experiment design.


Figure 3.1: 3D Model of the experiment on (table)


Figure 3.2: Flowchart showing manufacturing

## CHAPTER 4

## RESULTS

This final section presents obtained results. By utilizzing the kinematic analysis we

obtained the link lengths resulting in constant velocity mechanism as:

Link | Link length (cm)
OA | 13
CD | 9
AC | 11
AB | 39.5
DO | 5

Table 4.1: Final link lengths

Furthermore plots for slider velocity and acceleration were obtained using Simscape.


Figure 4.1: Slider Velocity


Figure 4.2: Slider acceleration

## CHAPTER 5

## CONCLUSION AND FUTURE WORK

The complete analysis of the mechanism(s) was performed using applicable method and

software. 3D CAD model of the mechanism was created to facilitate better visualisation.

Various design considerations were addressed and manufacturing workflow and plan

were accomplished as a prerequisite to manufacturing. Also, the BoM was prepared and

materials acquisition from the vendor is in process.

In the near future we shall start the manufacturing process based on the work that has

been already accomplished by now. After completing the manufacturing rigorous testing

will be done on the mechanism and corrections be made accordingly. In the end we will

work on preparing the documentation for the product.

## APPENDIX A

## CODE LISTING

The code used for carrying out this work is presented here. Due due to the high

volume of the code involved in this project, it is also hosted on GitHub for clearity at

https://github.com/AakashSYadav/BTP with complete documentation.

## A.1 Six-bar mechanism (Python)

1 # http://firsttimeprogrammer.blogspot.com/2015/02/crankshaft-

connecting-rod-and-piston.html

2

3 # import matplotlib.animation as animation

4 # import matplotlib.pyplot as plt

5 # from sympy import symbols, Eq, solve

6 import numpy as np

7 import time

8 import math

9 import csv

10

11 # plt.style.use(’ggplot’)

12 link_a_pivot = (0,-10)

13 link_p_pivot = (0,0)

14 # x, y, h = symbols(’x y h’)

15

16 class My_mechanism(object):

17

18 | # The init function
19 | def __init__(self,a,b,p,q,omega):
20 | self.a = a | # Rod a
21 | self.b = b | # Rod b
22 | self.p = p | # Rod p
23 | self.q = q | # Rod q
24 | self.omega = omega | # Angular speed of rod a in rad

/s

25 | self.theta0 = 0 | # Initial angular position of

rod a theta()

26 | self.set0 = (0,-100) | # for selecting one of the two

solutions

27 | self.k = 0.00001 | # Initial time for animation
28 | self.c_position = [] | # Piston position for animation
29 | self.c_speed = [] | # storing piston speed
30 | self.c_time = [] | # storing the time intervals
31 | self.pos_old = 0 | # old position of the piston for c_dot

calculation

32

33 | # Angular position of rod a as a function of time
34 | def theta(self,t):
35 | # if not all(t):
36 | # | raise ValueError(’Each time t must be greater than 0’)
37 | theta = self.theta0 + self.omega*t
38 | return theta

39

40 | def rod_p_position(self,t):
41 | p_y = self.p*np.sin(self.theta(t))
42 | p_x = self.p*np.cos(self.theta(t))
43 | return p_x,p_y

44

45 | def rod_q_position(self,t):
46 | px,py = self.rod_p_position(t)
47 | ax,ay = link_a_pivot
48 | c = ((self.p**2-px**2-py**2) - (self.a**2-ax**2-ay**2)) /
| (2*(ax-px))
49 | d = (py-ay)/(ax-px)
50 | D = (d*(px-c)+py)**2 - (1+d**2)*(py**2 + (px-c)**2 - self.p
| **2)
51 | if D<0:
52 | print("complex")
53 | raise Exception(’complex’)
54 | D2 = D**0.5
55 | y0 = (d*(px-c)+py+D2)/(1+d**2)
56 | y1 = (d*(px-c)+py-D2)/(1+d**2)
57 | x0 = c+d*y0
58 | x1 = c+d*y1
59 | set1=(x0,y0)

60 | set2=(x1,y1)
61 | # print(set1,set2)

62

63 | dist1 = math.hypot(set1[0] - self.set0[0], set1[1] - self.
| set0[1])
64 | dist2 = math.hypot(set2[0] - self.set0[0], set2[1] - self.
| set0[1])
65 | if dist1<dist2:
66 | self.set0=set1
67 | return set1[0],set1[1]
68 | else:
69 | self.set0=set2
70 | return set2[0],set2[1]

71

72 | def piston_position(self,t):
73 | q_x,q_y = self.rod_q_position(t)
74 | h0 = q_x+(self.b**2 - (q_y-link_a_pivot[1])**2)**0.5
75 | return h0

76

77 | # Piston speed
78 | def c_dot(self,t):
79 | c_x = self.piston_position(t)
80 | # c_dot = (c_x-self.pos_old)/0.05
81 | c_dot = abs(c_x-self.pos_old)/0.01 | # dt = 0.01
82 | self.pos_old = c_x
83 | return c_dot

84

85 | def velocity_params(self):
86 | while self.k<3.5: # to get one complete cycle
87 | speed = self.c_dot(self.k)
88 | self.k+=0.01

89

90 | """
91 | Uncomment the below 3 lines and comment the rest
92 | to collect data for a single set of params using "c_out_2.

py"

93 | """
94 | # with open(’oneP_best2.csv’, mode=’a’) as label_file:
95 | # | label_writer = csv.writer(label_file, delimiter=’,’,

quotechar=’"’, quoting=csv.QUOTE_MINIMAL)

96 | # | label_writer.writerow([self.k,speed])

97

98 | if self.k>0.4 and self.k<2.1:# store the ROI
99 | self.c_speed.append(speed)
100 | self.c_time.append(self.k)

101

102 | # print(self.c_speed)
103 | maxi = []
104 | mini = []
105 | for i in range(1,len(self.c_speed)-1):
106 | # local maxima
107 | if self.c_speed[i]>self.c_speed[i+1] and self.c_speed[i]>
| self.c_speed[i-1]:
108 | maxi.append(self.c_speed[i])
109 | # print("max",self.c_speed[i])
110 | # local minima
111 | if self.c_speed[i]<self.c_speed[i+1] and self.c_speed[i]<
| self.c_speed[i-1]:
112 | mini.append(self.c_speed[i])
113 | # print("min",self.c_speed[i])
114 | # print(self.a,self.b,self.p,self.q,max(maxi),min(mini))
115 | with open(’data_best.csv’, mode=’a’) as label_file:
116 | label_writer = csv.writer(label_file, delimiter=’,’,
| quotechar=’"’, quoting=csv.QUOTE_MINIMAL)
117 | label_writer.writerow([self.a,self.b,self.p,self.q,max(
| maxi),min(mini)])
118 | mini.clear()
119 | maxi.clear()
120 | self.c_speed.clear()
121 | self.time.clear()

1 from crankshaft import *

2 import time

3

4 initial_time = time.time()

5 # #a,b,p,q,omega

6 # best

7 for a in range(20,35):

8 | for b in range(70,80):
9 | for p in range(15,25):

10 | for q in range(15,30):
11 | m = My_mechanism(a,b,p,q,2)
12 | try:
13 | m.velocity_params()
14 | except Exception:
15 | continue

16

17 print("Processing time : ",time.time()-initial_time,"s")

## REFERENCES

1. (2017). MATLAB version 9.3.0.713579 (R2017b). The Mathworks, Inc., Natick, Mas-sachusetts.
2. A. Ghosh and A. K. Mallik, Theory of mechanisms and machines. Affiliated East-West Press Private Limited, 2002.
3. M. Hohenwarter, M. Borcherds, G. Ancsin, B. Bencze, M. Blossier, A. Delobelle,
C. Denizet, J. Éliás, A. Fekete, L. Gál, Z. Konecný ˇ , Z. Kovács, S. Lizelfelner,
B. Parisse, and G. Sturr (2013). GeoGebra 4.4. http://www.geogebra.org.
4. R. L. Norton, Kinematics and dynamics of machinery. McGraw-Hill Higher Education, 2011.
5. Python Core Team (2018). Python: A dynamic, open source programming language. Python Software Foundation. URL https://www.python.org/.
6. J. J. Uicker, G. R. Pennock, J. E. Shigley, et al., Theory of machines and mechanisms, volume 1. Oxford University Press New York, NY, 2011.

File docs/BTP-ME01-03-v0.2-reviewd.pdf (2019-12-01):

## Design and Fabrication of Experiment for Dynamic Analysis of Mechanisms

submitted in partial fulfilment of the requirements for the degree of

BACHELOR OF TECHNOLOGY
in
MECHANICAL ENGINEERING
by

### AAKASH ME16B001 A. AKHIL ME16B003

### Supervisor(s) Dr. Sriram Sundar


### DEPARTMENT OF MECHANICAL ENGINEERING INDIAN INSTITUTE OF TECHNOLOGY TIRUPATI December 2019

## BONA FIDE CERTIFICATE

This is to certify that the thesis titled Design and Fabrication of Experiment for Dynamic Analysis of Mechanisms, submitted by Aakash and A. Akhil, to the Indian Institute of Technology, Tirupati, for the award of the degree of Bachelor of Technology, is a bona fide record of the research work done by him under our supervision. The contents of this thesis, in full or in parts, have not been submitted to any other Institute or University for the award of any degree or diploma.

Place: Tirupati
Date: 08-12-2019

Dr. Sriram Sundar
Guide
Assistant Professor
Department of Mechanical
Engineering
IIT Tirupati - 517501

## ACKNOWLEDGEMENTS

Thanks to all those who helped us during the course of our B.Tech. project at IIT Tirupati. We are thankful to and fortunate enough to get constant encouragement, support and guidance from Dr. Sriram Sundar of Mechanical Engineering Department which helped us in successfully completing first phase our project work. We would also like to extend our sincere esteems to all staff in laboratory for their timely support.

To our families, thank you for encouraging us in all of our pursuits and inspiring us to follow our dreams. We are especially grateful to our parents, who supported us emotionally and financially.

i

## ABSTRACT

KEYWORDS: Slider Crank Mechanism; Four bar mechanism; Six-bar mechanism; Dynamic analysis; Kinematic analysis; Simulation.

setup.

To design and fabricate an experimental setup for static, kinematic and dynamic analysis of mechanism(s). This will integrate the theoretical knowledge with the practical experiment, giving learner a chance to carry out the analysis experimentally, to plot the results, and most importantly, to bolster their understanding by providing them the opportunity to match the analytical results with the actual experimental results. The setup will have retrofitted parts in order to let the student carry out multiple experiments in the same

ii

This is abstract .

# It should tell in shoot what you

## have

done . | The first sentence is an objective . | Please rewrite this section

for abstract .

## TABLE OF CONTENTS

ACKNOWLEDGEMENTS; ABSTRACT; LIST OF FIGURES; ABBREVIATIONS; 1 INTRODUCTION; 1.1 Motivation and Objective .......................; 1.2 Present method(s) and Challenges ..................; 2 ANALYSIS OF MECHANISMS; 2.1 Mathematical Formulation ......................; 2.1.1 Slider crank mechanism ...................; 2.1.2 Four bar mechanism .....................; 2.1.3 Six bar mechanism ......................; 2.2 Kinematic analysis ..........................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

2. I kinematic analysis
2.lil Math formulation
2.t.li Slider crank .
2 Using commercial
Lol .
software

## LIST OF FIGURES

1.1 CAD model of the mechanism | 1
1.2 Three possible configurations of the mechanism: (1) Four bar, (2) Slider
crank and (3) Six bar | | 2
2.1 Slider crank mechanism | | 3
2.2 Free Body Diagram of link OA, AB and slider | | 5
2.3 Four bar mechanism | | 6
2.4 Six bar mechanism | | 7
2.5 Snapshot from GeoGebra showing the mechanism (left) and the velocity
profile (right) | | 7
2.6 Output window from Python for kinematic simulation ........ | 8
2.7 CAD model in MATLAB Simscape | | 9
2.8 4 x 4 | | 10

iv

## ABBREVIATIONS

The following list describes the significance of various abbreviations and acronyms used throughout the report.

KDM | Kinematics and Dynamics of Machinery
PMSM | Permanent Magnet Synchronous Motor
CAD | Computer Aided Design
CSV | Comma Seperated Values
FBD | Free Body Diagram

v

## CHAPTER 1

## INTRODUCTION

## 1.1 Motivation and Objective

The study of the ME2206 Kinematics and Dynamics of Machinery lies at the very core of a mechanical engineering background. Although, little has changed in the way the subject is presented, our methodology brings the subject alive and current. We present the design and fabrication of a novel experimental setup for carrying out static, kinematic

setup.; undergraduate students taking the course.; this part has; ← - to be emphasised; in report as well as; slides .; A single exp; for; static,; kinematic & dynamic analysis.

and dynamic analysis of mechanism (Figure 1.1). The mechanism is designed to be configurable to three different types of mechanisms namely - four bar, slider crank and six bar depending on the use case as shown in Figure 1.2. The mechanism has retrofitted parts (different link lengths and sliders) to facilitate multiple experiments in the same

The learner gets to "play" with the mechanism parameters and immediately see their effects. This will enhance one’s grasp of the concepts and the development of analytical skills. Hence greatly supplementing and reinforcing the theoretical understanding of the


Figure 1.1: CAD model of the mechanism

## 1.2 Present method(s) and Challenges

In the present scenario finding relevant mechanisms integrated with different sensor measurement and data acquisition is hard to find. Almost all the mechanisms that are

(ME 2206 )

n


Figure 1.2: Three possible configurations of the mechanism: (1) Four bar, (2) Slider crank and (3) Six bar

available off the self are available only for demonstrations purpose (not providing any measurement) and not as an experiment.

In Chapter 2 we present thoroughly all the methodologies used in designing and modelling the mechanism. This includes both the analysis carried out by analytical as well as numerical method. In the chapter that follows we bring out the various design considerations that has to be taken into account while manufacturing the product. The final two sections present the result(s) and the conclusion(s).

off-the-shelf | does | have
o | . | =

You can also

say that doing static, kinematics dynamic analysis
tapability .
with some mechanism
follows the
footsteps of § | how it is done
§ | in theory .
better
appreciation of
concepts .

## CHAPTER 2

## ANALYSIS OF MECHANISMS

## 2.1 Mathematical Formulation

In this section we bring out the equations of motion associated with the three different mechanisms. These equations are used to carry out the kinematic and dynamics method theoretically, which then in turn be compared with the numerical solutions obtained by other simulation tools.

### 2.1.1 Slider crank mechanism

The equations of motion pertaining to the slider crank mechanism are presented in this subsection.

~

VB/A =~

VB ~
VA | (2.1)

For link OA we have

~

VA/O = w~ AO ⇥~rA/O =~
VA | (2.2)


Figure 2.1: Slider crank mechanism

Since ’O’ is ground link we have ~

VO = 0 =) ~

VA/O =~

VA ~

VO =~
VA. As point B lies on
the slider and is moving leftwards it will have velocity along the negative x-direction i.e.

~

VB = VBˆi; because w~ AO = wAOˆ
k. For link AB we have

~

VB/A = w~ BA ⇥~rB/A | (2.3)

Substituting equation 2.3 in equation 2.2 we obtain

w~ BA ⇥~rB/A =~
VB ~
VA | (2.4)

Using equation 2.4 we can find wBA and VB. For finding the accelerations we can write

~aA/O =~aA =~at

A +~an
A | (2.5a)

~at
A =~a ⇥~r | (2.5b)

~an
A = w~ ⇥w~ ⇥~r | (2.5c)

where, ~at

A and ~an
A denote the tangential and normal acceleration of point A. As point B lies on the slider, we have ~aB = aBˆi.

~aB/A =~at

B/A +~an
B/A =~aB ~aA | (2.6)

Using the above equation we can find aBA and ~aB.

Force balance for link OA
FOX +FAX = 0 | (2.7a)
FOY +FAY = m1g | (2.7b)

IAO~aAO =~rC1O ⇥m1g( ˆj)+~rA/O ⇥~
FA | (2.7c)

where, ~; FAX ˆi+~; FAX = FBX; FBY = FAY +m2g; FBX ˆi+~; FBY +m3g = N; m3aB = FBX; faith 4revolute joints⁾

Figure 2.2: Free Body Diagram of link OA, AB and slider

FAY ˆj. Similarly for link AB we have

IBA~aB/A =~rC2/A ⇥m2g( ˆj)+~rB/A ⇥~

FBY ˆj. Performing force balance for the slider

2.1.2 Four bar mechanism


Figure 2.3: Four bar mechanism

~

VA/C = w~ AC ⇥~rA/C =~
VA ~

VC = w~ AO ⇥~rA/O w~ CD ⇥~rC/D (2.11)

Using the above equation we can find wCD and wAC.

~aA/O =~aA =~at

A +~an
A | (2.12a)

~aC/D =~aC =~at

C +~an
C | (2.12b)

~aA/C =~at

A/C +~an
A/C =~aA ~aC | (2.13)

Here~at =~a ⇥~r and ~an = w~ ⇥w~ ⇥~r. Using the above equations we can find aAC and aCD

### 2.1.3 Six bar mechanism

In this section we present the methodology employed in order to simulate the kinematics of the various mechanisms. In order to carry out the preliminary analysis of the mechanism we used the GeoGebra, which is an interactive math and geometry software. This

-_


Figure 2.4: Six bar mechanism

provided the coarse link lengths required for having the least deviant constant velocity mechanism as shown in Figure 2.5. Once the coarse link lengths were obtained, we developed an in-house Python code that can do iterations on the link lengths so as to minimise any fluctuations in the constant velocity mechanism. The visual output of the Python simulation can be seen in Figure 2.6 while rest of the simulation data is store in a CSV file.


Figure 2.5: Snapshot from GeoGebra showing the mechanism (left) and the velocity profile (right)


Figure 2.6: Output window from Python for kinematic simulation

### 2.2.1 GeoGebra Modelling

### 2.2.2 Python Simulation

## 2.3 Dynamic analysis

For performing the dynamic analysis of the mechanism we used MATLAB Simscape Mechanical package. The CAD was created in the package itself and analysed the same for various forces, torques, acceleration and velocities by taking the material as aluminium (Figure 2.7, ??). This analysis is necessary in order to ease the process of selection of actuator, material and the sensor system.

# lldhaorks'

O

O


Figure 2.7: CAD model in MATLAB Simscape

# Very small

# numbers ⁻

Not; at all; readable i; small '; can; 't get anything from; que figs .

at A-1.jpg

on figis

outof

## CHAPTER 3

## DESIGN FOR MANUFACTURING

## 3.1 Design considerations

** TBD **

## 3.2 Material Selection

** TBD **

## CHAPTER 4

## RESULTS

TBD

## CHAPTER 5

## CONCLUSION AND FUTURE WORK

The complete analysis of the mechanism(s) was performed using applicable method and software. 3D CAD model of the mechanism was created to facilitate better visualisation. Various design considerations were addressed and manufacturing workflow and plan were accomplished as a prerequisite to manufacturing. Also, the BoM was prepared and materials acquisition from the vendor is in process.

In the near future we shall start the manufacturing process based on the work that has been already accomplished by now. After completing the manufacturing rigorous testing will be done on the mechanism and corrections be made accordingly. In the end we will work on preparing the documentation for the product.

## APPENDIX A

## CODE LISTING

The code used for carrying out this work is presented here. Although due to the high volume of the code involved in this project, it is hosted with complete documentation on GitHub at https://github.com/AakashSYadav/BTP .

## A.1 Six-bar mechanism (Python)

1 # http://firsttimeprogrammer.blogspot.com/2015/02/crankshaft-connecting-rod-and-piston.html

2
3 # import matplotlib.animation as animation 4 # import matplotlib.pyplot as plt
5 # from sympy import symbols, Eq, solve
6 import numpy as np
7 import time
8 import math
9 import csv

10
11 # plt.style.use(’ggplot’) 12 link_a_pivot = (0,-10)
13 link_p_pivot = (0,0)
14 # x, y, h = symbols(’x y h’)

15
16 class My_mechanism(object):

17
18 | # The init function
19 | def __init__(self,a,b,p,q,omega):
20 | self.a = a | # Rod a
21 | self.b = b | # Rod b
22 | self.p = p | # Rod p
23 | self.q = q | # Rod q
24 | self.omega = omega | # Angular speed of rod a in rad
/s

25 | self.theta0 = 0 | # Initial angular position of
rod a theta()
26 | self.set0 = (0,-100) | # for selecting one of the two
solutions
27 | self.k = 0.00001 | # Initial time for animation
28 | self.c_position = [] | # Piston position for animation
29 | self.c_speed = [] | # storing piston speed
30 | self.c_time = [] | # storing the time intervals
31 | self.pos_old = 0 # old position of the piston for c_dot
calculation

32
33 | # Angular position of rod a as a function of time
34 | def theta(self,t):
35 | # if not all(t):
36 | # | raise ValueError(’Each time t must be greater than 0’)
37 | theta = self.theta0 + self.omega*t
38 | return theta

39
40 | def rod_p_position(self,t):
41 | p_y = self.p*np.sin(self.theta(t))
42 | p_x = self.p*np.cos(self.theta(t))
43 | return p_x,p_y

44
45 | def rod_q_position(self,t):
46 | px,py = self.rod_p_position(t)
47 | ax,ay = link_a_pivot
48 | c = ((self.p**2-px**2-py**2) - (self.a**2-ax**2-ay**2)) /
(2*(ax-px))
49 | d = (py-ay)/(ax-px)
50 | D = (d*(px-c)+py)**2 - (1+d**2)*(py**2 + (px-c)**2 - self.p
**2)
51 | if D<0:
52 | print("complex")
53 | raise Exception(’complex’)
54 | D2 = D**0.5
55 | y0 = (d*(px-c)+py+D2)/(1+d**2)
56 | y1 = (d*(px-c)+py-D2)/(1+d**2)
57 | x0 = c+d*y0
58 | x1 = c+d*y1
59 | set1=(x0,y0)

60 | set2=(x1,y1)
61 | # print(set1,set2)

62
63 | dist1 = math.hypot(set1[0] - self.set0[0], set1[1] - self.
set0[1])
64 | dist2 = math.hypot(set2[0] - self.set0[0], set2[1] - self.
set0[1])
65 | if dist1<dist2:
66 | self.set0=set1
67 | return set1[0],set1[1]
68 | else:
69 | self.set0=set2
70 | return set2[0],set2[1]

71
72 | def piston_position(self,t):
73 | q_x,q_y = self.rod_q_position(t)
74 | h0 = q_x+(self.b**2 - (q_y-link_a_pivot[1])**2)**0.5
75 | return h0

76
77 | # Piston speed
78 | def c_dot(self,t):
79 | c_x = self.piston_position(t)
80 | # c_dot = (c_x-self.pos_old)/0.05
81 | c_dot = abs(c_x-self.pos_old)/0.01 # dt = 0.01
82 | self.pos_old = c_x
83 | return c_dot

84
85 | def velocity_params(self):
86 | while self.k<3.5: # to get one complete cycle
87 | speed = self.c_dot(self.k)
88 | self.k+=0.01

89
90 | """
91 | Uncomment the below 3 lines and comment the rest
92 | to collect data for a single set of params using "c_out_2.
py"
93 | """
94 | # with open(’oneP_best2.csv’, mode=’a’) as label_file:
95 | # | label_writer = csv.writer(label_file, delimiter=’,’,
quotechar=’"’, quoting=csv.QUOTE_MINIMAL)

96 | # | label_writer.writerow([self.k,speed])

97
98 | if self.k>0.4 and self.k<2.1:# store the ROI
99 | | self.c_speed.append(speed)
100 | | self.c_time.append(self.k)

101
102 | # print(self.c_speed)
103 | maxi = []
104 | mini = []
105 | for i in range(1,len(self.c_speed)-1):
106 | # local maxima
107 | if self.c_speed[i]>self.c_speed[i+1] and self.c_speed[i]>
self.c_speed[i-1]:
108 | | maxi.append(self.c_speed[i])
109 | | # print("max",self.c_speed[i])
110 | # local minima
111 | if self.c_speed[i]<self.c_speed[i+1] and self.c_speed[i]<
self.c_speed[i-1]:
112 | | mini.append(self.c_speed[i])
113 | | # print("min",self.c_speed[i])
114 | # print(self.a,self.b,self.p,self.q,max(maxi),min(mini))
115 | with open(’data_best.csv’, mode=’a’) as label_file:
116 | label_writer = csv.writer(label_file, delimiter=’,’,
quotechar=’"’, quoting=csv.QUOTE_MINIMAL)
117 | label_writer.writerow([self.a,self.b,self.p,self.q,max(
maxi),min(mini)])
118 | mini.clear()
119 | maxi.clear()
120 | self.c_speed.clear()
121 | self.time.clear()

1 from crankshaft import * 2 import time

3
4 initial_time = time.time() 5 # #a,b,p,q,omega
6 # best
7 for a in range(20,35):
8 | for b in range(70,80):
9 | for p in range(15,25):

10 | for q in range(15,30):
11 | m = My_mechanism(a,b,p,q,2)
12 | try:
13 | m.velocity_params()
14 | except Exception:
15 | continue

16
17 print("Processing time : ",time.time()-initial_time,"s")

## REFERENCES

Please populate this dsnp.


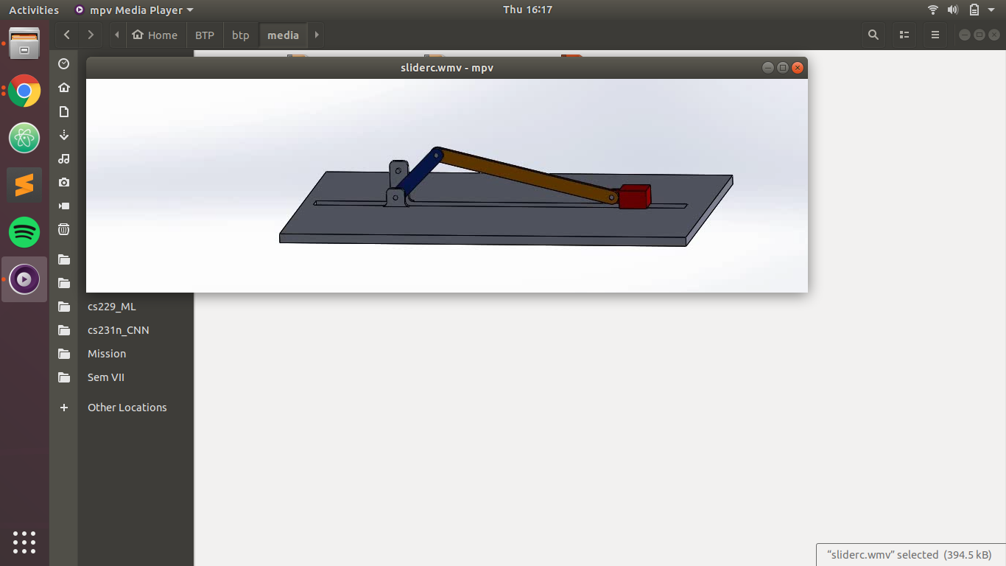
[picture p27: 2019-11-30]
media/med_report/Screenshot from 2019-11-21 16-17-36.png

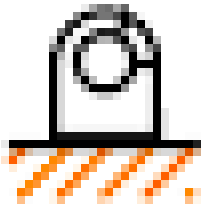
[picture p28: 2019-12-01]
media/med_report/ggb_figures/ground.png

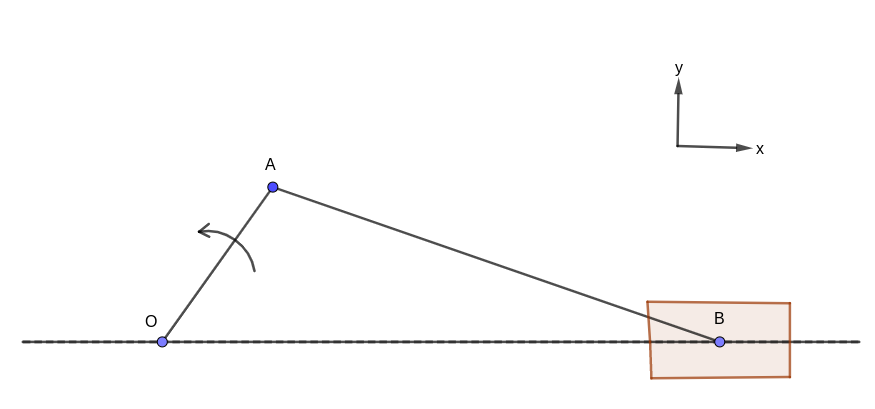
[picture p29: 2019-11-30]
media/med_report/ggb_figures/ggbr_sliderCrank.png

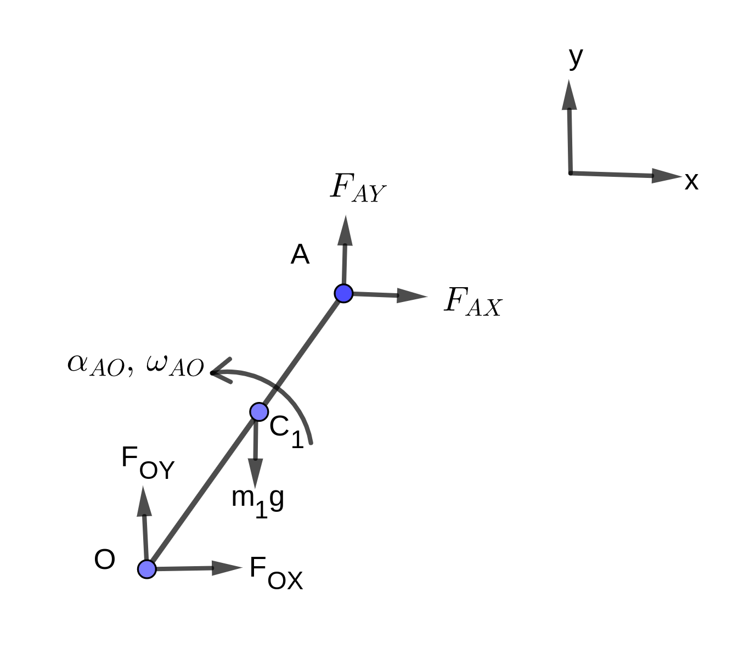
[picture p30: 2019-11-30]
media/med_report/ggb_figures/ao.png

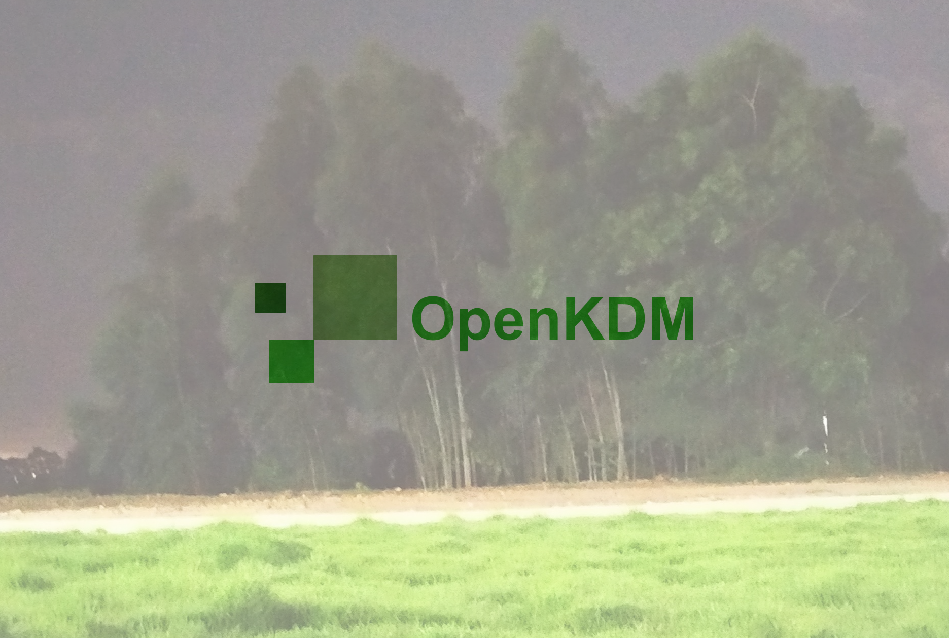
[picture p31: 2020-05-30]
rpi/openkdm_wallpaper.png

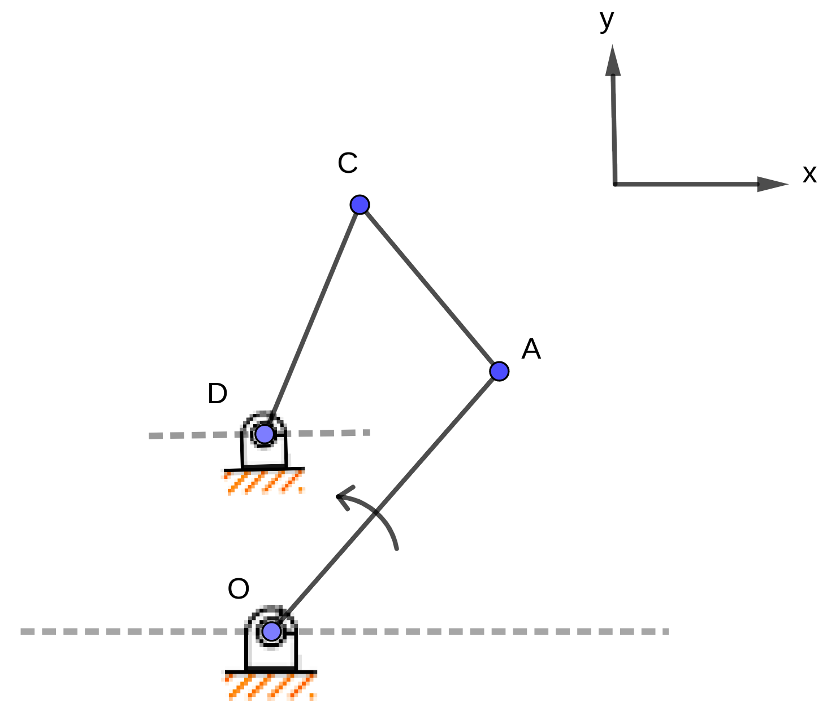
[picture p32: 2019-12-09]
media/4bar3.png

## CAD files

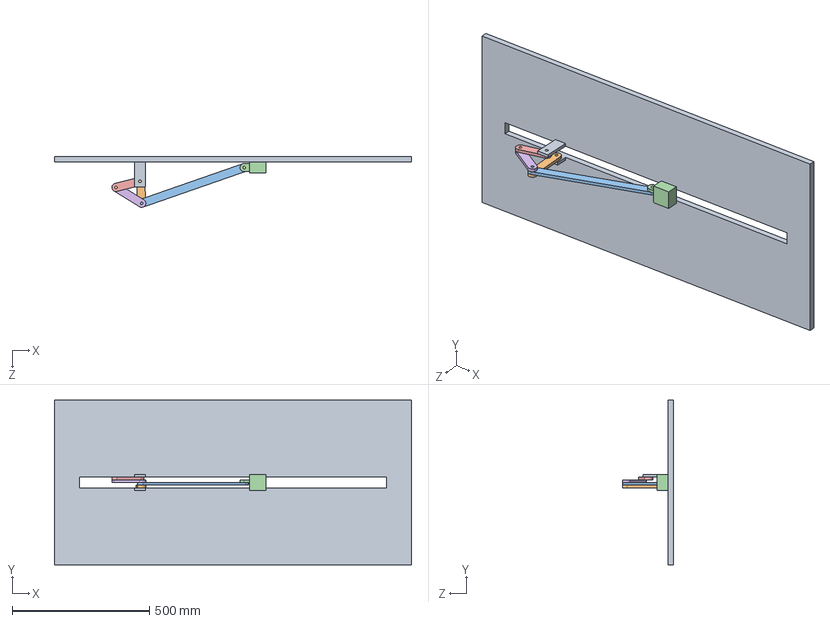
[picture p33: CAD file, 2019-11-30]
CAD/0.0/Assem1.SLDASM
1300.0 x 600.0 x 184.8 mm
ground
a
b
slider
p
q
pin2 x 4
pin3

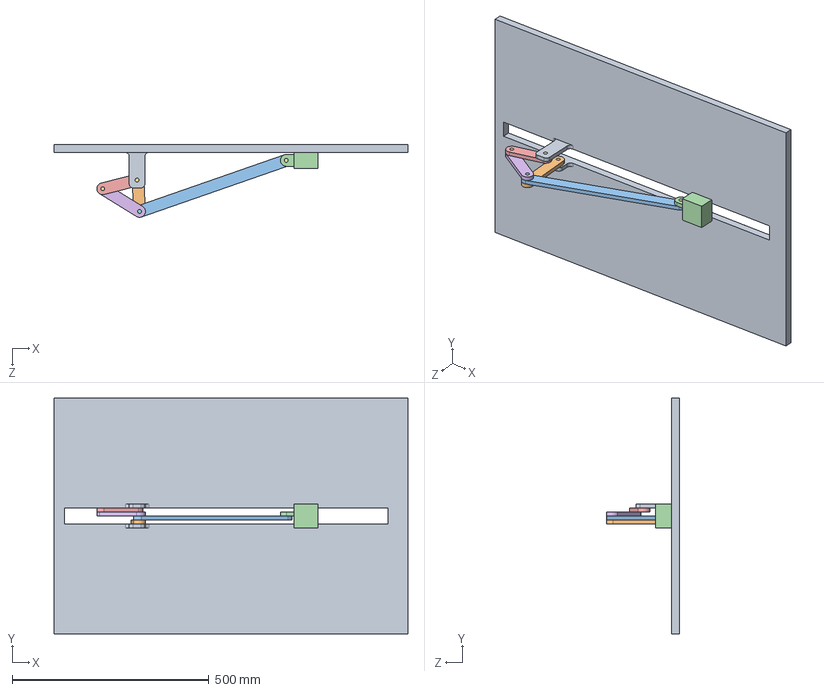
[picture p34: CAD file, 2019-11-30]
CAD/Assem1.SLDASM
900.0 x 600.0 x 184.8 mm
ground
a
b
slider
p
q
pin2 x 4
pin3

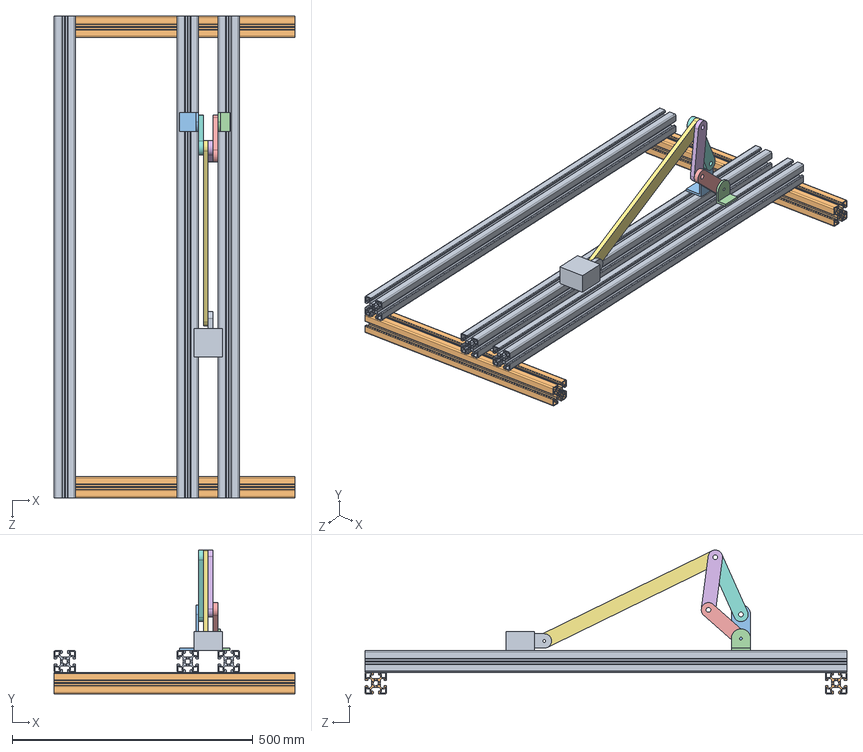
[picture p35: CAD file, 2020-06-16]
CAD/cad/cad_backup/btp2020/btp2020.SLDASM
500.0 x 298.6 x 1000.0 mm
frame1000 x 3
frame500 x 2
c1
c2
p
q
b
a
slider

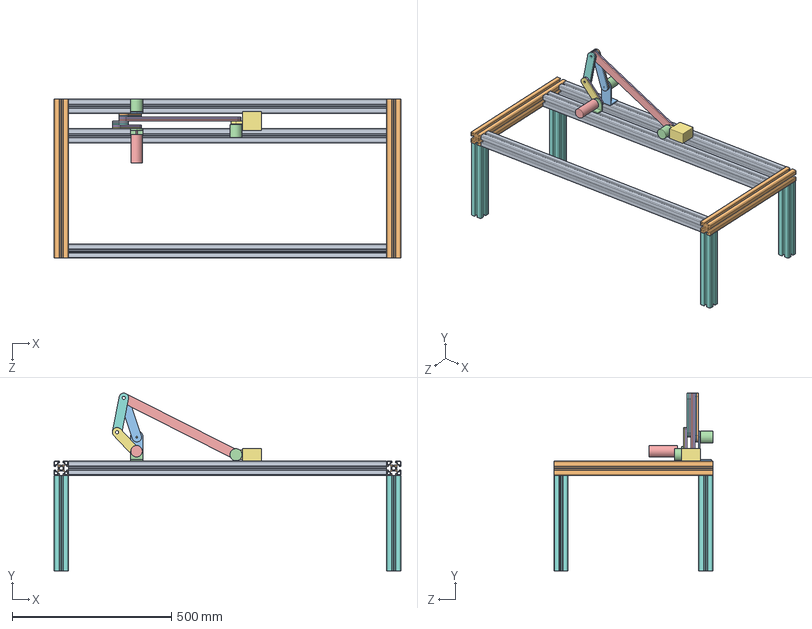
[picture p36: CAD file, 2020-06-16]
CAD/cad/cad_backup/btp2020/final_btp.SLDASM
1090.0 x 558.4 x 501.0 mm
frame1000 x 3
frame500 x 2
c1
c2
motor
cdnew1
cdnew2
acnew1
acnew2
anew2
anew1
encoder x 2
abnew1
abnew2
slider
leg x 4

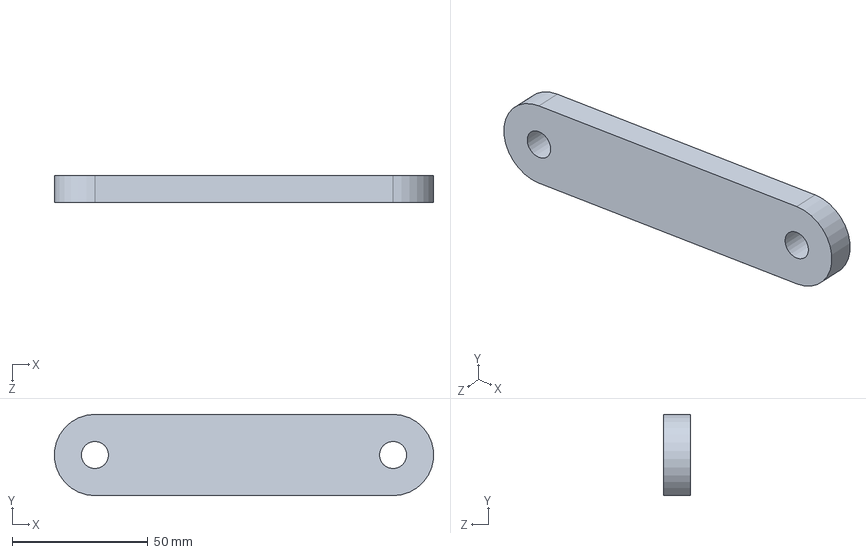
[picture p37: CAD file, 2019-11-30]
CAD/0/q.SLDPRT
139.8 x 30.0 x 10.0 mm

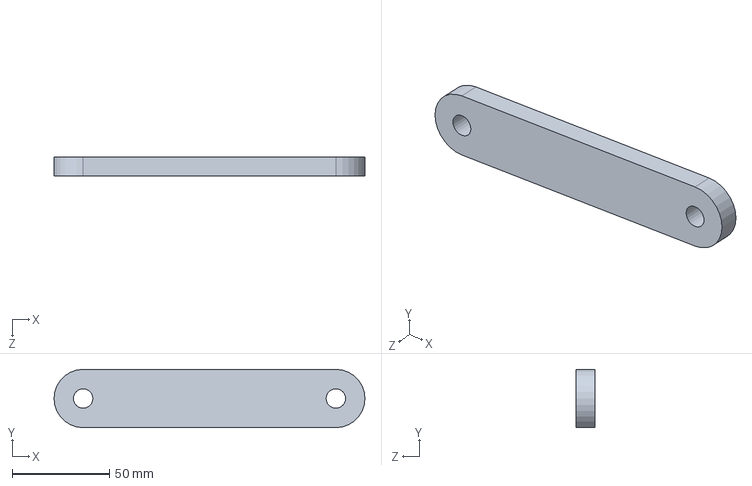
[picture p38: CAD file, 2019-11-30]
CAD/1/a.SLDPRT
160.0 x 30.0 x 10.0 mm

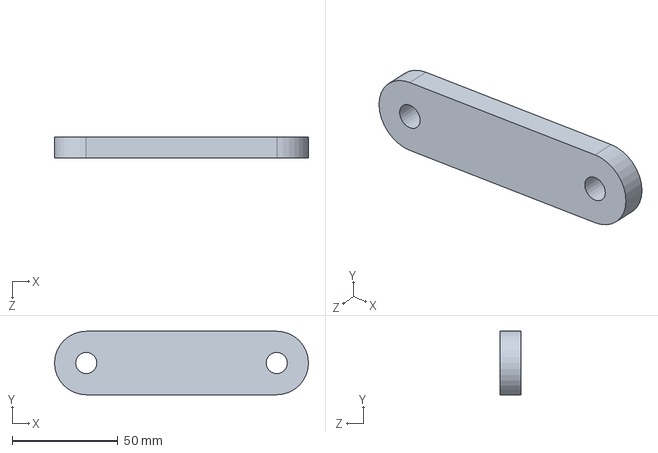
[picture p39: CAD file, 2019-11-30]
CAD/btp/p.SLDPRT
120.0 x 30.0 x 10.0 mm

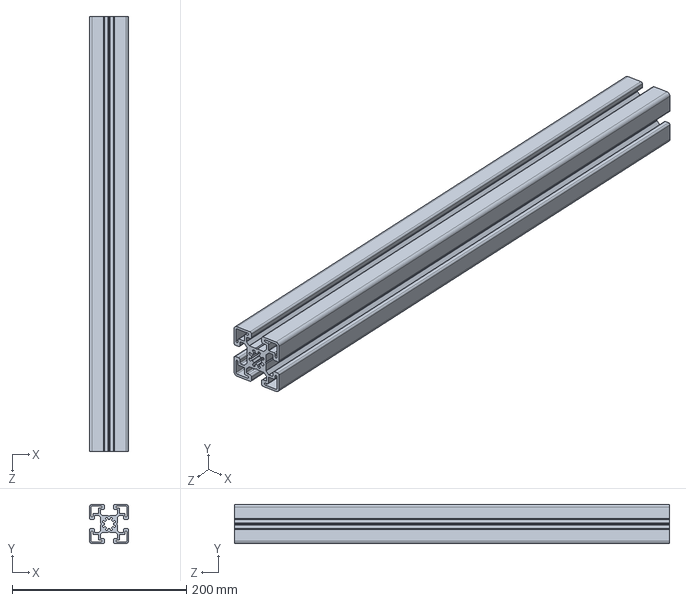
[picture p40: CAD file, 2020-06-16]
CAD/cad/cad_backup/btp2020/frame500.SLDPRT
45.0 x 45.0 x 500.0 mm

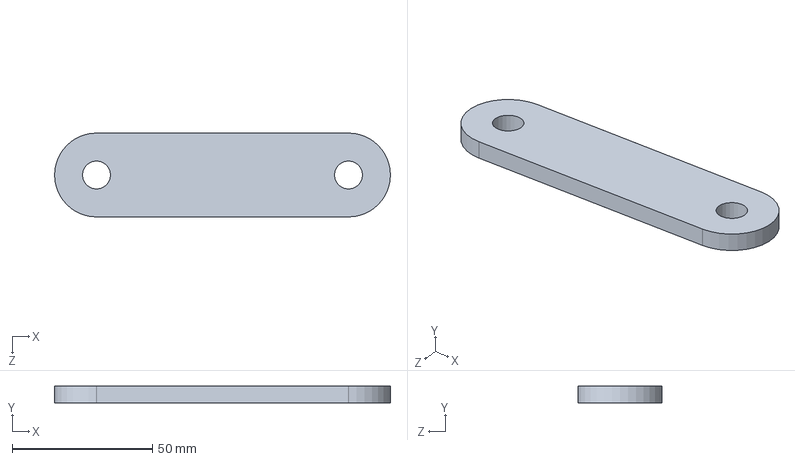
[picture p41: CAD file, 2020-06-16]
CAD/cad/cdnew2.SLDPRT
120.0 x 6.00 x 30.0 mm

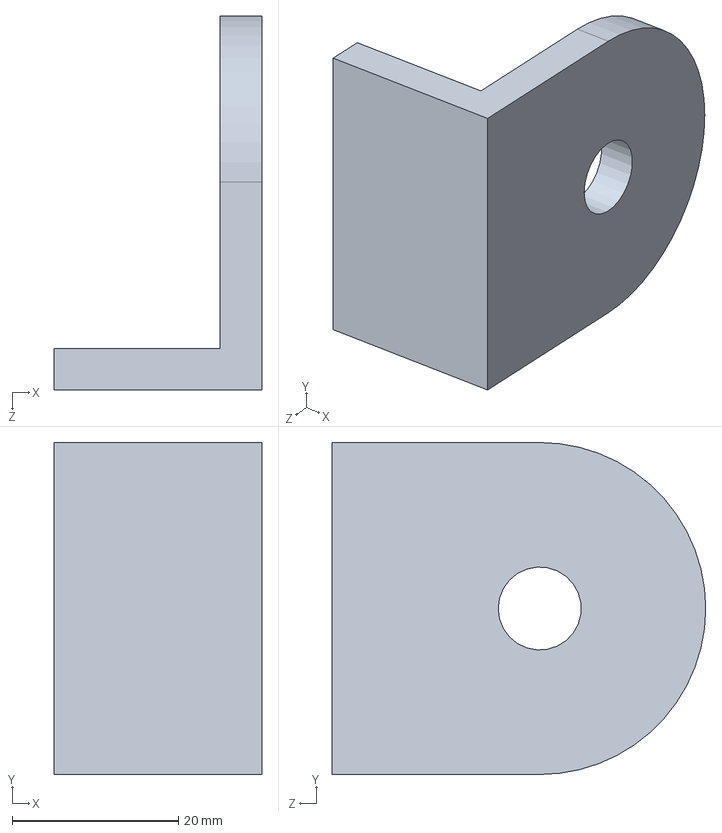
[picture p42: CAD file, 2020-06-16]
CAD/CAD_btp2020/c2.SLDPRT
25.0 x 40.0 x 45.0 mm

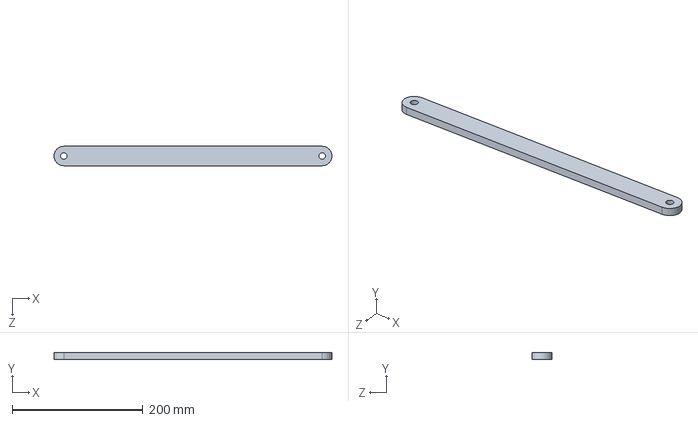
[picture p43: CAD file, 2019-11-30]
CAD/0.0/b.SLDPRT
425.0 x 10.0 x 30.0 mm

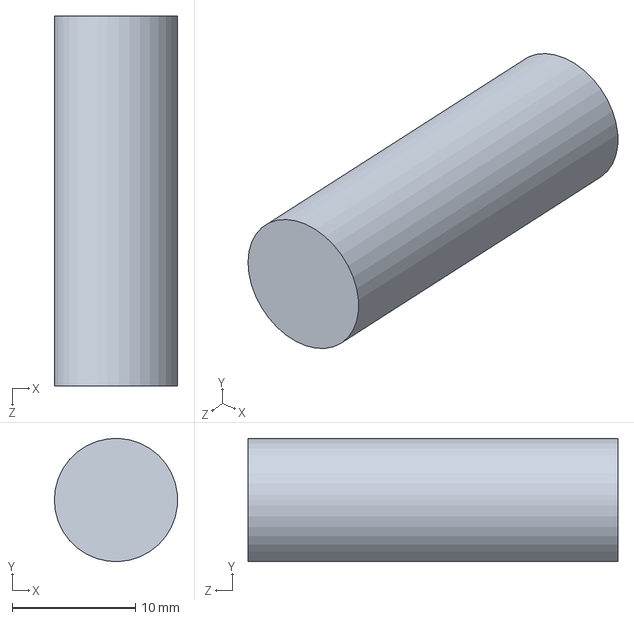
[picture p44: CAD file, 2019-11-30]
CAD/0/pin3.SLDPRT
10.0 x 9.99 x 30.0 mm

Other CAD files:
CAD/CAD_btp2020/btp2020.SLDASM
CAD/0/Assem1.SLDASM
CAD/cad/cad_backup/btp/a.SLDPRT
CAD/0.0/a.SLDPRT
CAD/0.0/ground.SLDPRT
CAD/0.0/pin2.SLDPRT
CAD/0/a.SLDPRT
CAD/0/ground.SLDPRT
CAD/0/pin2.SLDPRT
CAD/0/slider.SLDPRT
CAD/1/ground.SLDPRT
CAD/1/pin2.SLDPRT
CAD/1/slider.SLDPRT
CAD/Assem1.SLDDRW
CAD/CAD_btp2020/c1.SLDPRT
CAD/CAD_btp2020/frame.SLDPRT
CAD/CAD_btp2020/frame1000.SLDPRT
CAD/CAD_btp2020/insert.SLDPRT
CAD/btp/Assem1.SLDDRW
CAD/btp/ground.SLDPRT
CAD/btp/pin2.SLDPRT
CAD/btp/slider.SLDPRT
CAD/cad/Assem1.SLDDRW
CAD/cad/Draw1.SLDDRW
CAD/cad/a.SLDPRT
CAD/cad/abnew1.SLDDRW
CAD/cad/abnew1.SLDPRT
CAD/cad/abnew2.SLDDRW
CAD/cad/abnew2.SLDPRT
CAD/cad/acnew1.SLDDRW
CAD/cad/acnew1.SLDPRT
CAD/cad/acnew2.SLDDRW
CAD/cad/acnew2.SLDPRT
CAD/cad/anew1.SLDDRW
CAD/cad/anew1.SLDPRT
CAD/cad/anew2.SLDDRW
CAD/cad/anew2.SLDPRT
CAD/cad/b.SLDPRT
CAD/cad/cad_backup/btp/Assem1.SLDDRW
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

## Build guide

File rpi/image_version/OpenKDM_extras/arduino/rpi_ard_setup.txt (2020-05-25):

# author @nimrobotics for OpenKDM
# (c) 2020

Download arduino-cli 0.10.0 (ARMv7 from https://github.com/arduino/arduino-cli/releases)
Copy to the bin: cp arduino-cli /bin/
Follow the setup https://www.devdungeon.com/content/arduino-cli-tutorial and install avr core

Install custom library by putting the extracted zip in /home/pi/Arduino/libraries folder

Example:
pi@raspberrypi:~/Desktop $ arduino-cli compile --fqbn arduino:avr:uno /home/pi/Desktop/serial_test
Sketch uses 3154 bytes (9%) of program storage space. Maximum is 32256 bytes.
Global variables use 252 bytes (12%) of dynamic memory, leaving 1796 bytes for local variables. Maximum is 2048 bytes.
pi@raspberrypi:~/Desktop $ arduino-cli upload --port /dev/ttyACM0 --fqbn arduino:avr:uno /home/pi/Desktop/serial_test

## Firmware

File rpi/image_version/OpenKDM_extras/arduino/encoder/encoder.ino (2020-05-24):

// Original: https://robu.in/product/orange-600-ppr-abz-3-phase-incremental-magnetic-rotary-encoder/
// modified @nimrobotics for OpenKDM 

//these pins can not be changed 2/3 are special pins
int encoderPin1 = 2;
int encoderPin2 = 3;

volatile int lastEncoded = 0;
volatile long encoderValue = 0;

long lastencoderValue = 0;

int lastMSB = 0;
int lastLSB = 0;

void setup() {
  Serial.begin (115200);

  pinMode(encoderPin1, INPUT); 
  pinMode(encoderPin2, INPUT);

  digitalWrite(encoderPin1, HIGH); //turn pullup resistor on
  digitalWrite(encoderPin2, HIGH); //turn pullup resistor on

  //call updateEncoder() when any high/low changed seen
  //on interrupt 0 (pin 2), or interrupt 1 (pin 3) 
  attachInterrupt(0, updateEncoder, CHANGE); 
  attachInterrupt(1, updateEncoder, CHANGE);

}

void loop(){ 
  //Do stuff here

  Serial.println(encoderValue);
  delay(100); //just here to slow down the output, and show it will work  even during a delay
}


void updateEncoder(){
  int MSB = digitalRead(encoderPin1); //MSB = most significant bit
  int LSB = digitalRead(encoderPin2); //LSB = least significant bit

  int encoded = (MSB << 1) |LSB; //converting the 2 pin value to single number
  int sum  = (lastEncoded << 2) | encoded; //adding it to the previous encoded value

  if(sum == 0b1101 || sum == 0b0100 || sum == 0b0010 || sum == 0b1011) encoderValue ++;
  if(sum == 0b1110 || sum == 0b0111 || sum == 0b0001 || sum == 0b1000) encoderValue --;

  lastEncoded = encoded; //store this value for next time
}

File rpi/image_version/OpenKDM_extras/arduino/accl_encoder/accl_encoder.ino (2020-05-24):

/*
 * https://www.electronicwings.com/arduino/mpu6050-interfacing-with-arduino-uno
 * Web: http://www.jarzebski.pl
 * (c) 2014 by Korneliusz Jarzebski
 * 
 * Modified @nimrobotics for OpenKDM
 * MPU6050 --> Uno
 * vcc --> 5v
 * gnd --> gnd
 * scl --> scl
 * sda --> sda
 */

#include <Wire.h>
#include <MPU6050.h>

MPU6050 mpu;

//encoder start
int encoderPin1 = 2;
int encoderPin2 = 3;

volatile int lastEncoded = 0;
volatile long encoderValue = 0;

long lastencoderValue = 0;

int lastMSB = 0;
int lastLSB = 0;
// encoder end

void setup() {
  // put your setup code here, to run once:
  Serial.begin(115200);
  Serial.println("Initialize MPU6050");

  while(!mpu.begin(MPU6050_SCALE_2000DPS, MPU6050_RANGE_2G))
  {
    Serial.println("Could not find a valid MPU6050 sensor, check wiring!");
    delay(500);
  }
  checkSettings();

  // encoder start
  pinMode(encoderPin1, INPUT); 
  pinMode(encoderPin2, INPUT);

  digitalWrite(encoderPin1, HIGH); //turn pullup resistor on
  digitalWrite(encoderPin2, HIGH); //turn pullup resistor on

  //call updateEncoder() when any high/low changed seen
  //on interrupt 0 (pin 2), or interrupt 1 (pin 3) 
  attachInterrupt(0, updateEncoder, CHANGE); 
  attachInterrupt(1, updateEncoder, CHANGE);
  // encoder end
}

void checkSettings()
{
  Serial.println();
  
  Serial.print(" * Sleep Mode:            ");
  Serial.println(mpu.getSleepEnabled() ? "Enabled" : "Disabled");
  
  Serial.print(" * Clock Source:          ");
  switch(mpu.getClockSource())
  {
    case MPU6050_CLOCK_KEEP_RESET:     Serial.println("Stops the clock and keeps the timing generator in reset"); break;
    case MPU6050_CLOCK_EXTERNAL_19MHZ: Serial.println("PLL with external 19.2MHz reference"); break;
    case MPU6050_CLOCK_EXTERNAL_32KHZ: Serial.println("PLL with external 32.768kHz reference"); break;
    case MPU6050_CLOCK_PLL_ZGYRO:      Serial.println("PLL with Z axis gyroscope reference"); break;
    case MPU6050_CLOCK_PLL_YGYRO:      Serial.println("PLL with Y axis gyroscope reference"); break;
    case MPU6050_CLOCK_PLL_XGYRO:      Serial.println("PLL with X axis gyroscope reference"); break;
    case MPU6050_CLOCK_INTERNAL_8MHZ:  Serial.println("Internal 8MHz oscillator"); break;
  }
  
  Serial.print(" * Accelerometer:         ");
  switch(mpu.getRange())
  {
    case MPU6050_RANGE_16G:            Serial.println("+/- 16 g"); break;
    case MPU6050_RANGE_8G:             Serial.println("+/- 8 g"); break;
    case MPU6050_RANGE_4G:             Serial.println("+/- 4 g"); break;
    case MPU6050_RANGE_2G:             Serial.println("+/- 2 g"); break;
  }  

  Serial.print(" * Accelerometer offsets: ");
  Serial.print(mpu.getAccelOffsetX());
  Serial.print(" / ");
  Serial.print(mpu.getAccelOffsetY());
  Serial.print(" / ");
  Serial.println(mpu.getAccelOffsetZ());
  Serial.println();
}

void loop()
{
  Vector rawAccel = mpu.readRawAccel();
  Vector normAccel = mpu.readNormalizeAccel();
  delay(50);
  Serial.print("Accln:");
  Serial.println(normAccel.YAxis);

  //  encoder start
  Serial.print("Angle:");
  Serial.println(encoderValue);
  // encoder end 
}

//function for encoder 
void updateEncoder(){
  int MSB = digitalRead(encoderPin1); //MSB = most significant bit
  int LSB = digitalRead(encoderPin2); //LSB = least significant bit

  int encoded = (MSB << 1) |LSB; //converting the 2 pin value to single number
  int sum  = (lastEncoded << 2) | encoded; //adding it to the previous encoded value

  if(sum == 0b1101 || sum == 0b0100 || sum == 0b0010 || sum == 0b1011) encoderValue ++;
  if(sum == 0b1110 || sum == 0b0111 || sum == 0b0001 || sum == 0b1000) encoderValue --;

  lastEncoded = encoded; //store this value for next time
}

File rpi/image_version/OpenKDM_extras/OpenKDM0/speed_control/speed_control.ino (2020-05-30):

/*
Connections of Drive and Arduino
Serial Port 0 is not used to connect to drive because its connected to USB-Serial and used to show information on console.

For Arduino Uno Software serial needs to be used as there is only one hardware serial port and its connected to USB-Serial. 
   Drive to Arduino UNO/Nano connections
   GND         -      GND
   RXD         -      D3
   TXD         -      D2

For arduino mega and other arduinos with multiple hardware serial port, any port other than 0 can be selected to connect the drive.

   Drive to Arduino Mega2560 connections
   GND         -      GND
   RXD         -      Tx1/Tx2/Tx3
   TXD         -      Rx1/Rx2/Rx3
   
*	This mode can be used when multiple motors are to be used to run at exactly the same RPM and same torque even though the voltage supply might be different.
*	Also in this mode the direction of the motor can be controlled digitally via modbus ASCII commands to run the dc servo motor in both directions

* For more information see : https://robokits.co.in/motor-drives-drivers/encoder-dc-servo/rhino-dc-servo-driver-50w-compatible-with-modbus-uart-ascii-for-encoder-dc-servo-motor
* 
* modified @nimrobotics for OpenKDM 
*/

#include<RMCS2303drive.h>

RMCS2303 rmcs;                    //object for class RMCS2303

SoftwareSerial myserial(2,3);     //Software Serial port For Arduino Uno. Comment out if using Mega.

int speed_rpm=4;

//parameter Settings "Refer datasheet for details"
byte slave_id=7;
int INP_CONTROL_MODE=257;           
int PP_gain=32;
int PI_gain=16;
int VF_gain=32;
int LPR=334;    //lines per rotation
int acceleration=0; 
int speed=speed_rpm*LPR;


long int Current_position;
long int Current_Speed;

void setup()
{
   rmcs.Serial_selection(1);       //Serial port selection:0-Hardware serial,1-Software serial
   rmcs.Serial0(9600);             //Set baudrate for usb serial to monitor data on serial monitor
   Serial.println("RMCS-2303 Speed control mode demo\r\n\r\n");

   //rmcs.begin(&Serial1,9600);    //Uncomment if using hardware serial port for mega2560:Serial1,Serial2,Serial3 and set baudrate. Comment this line if Software serial port is in use
   rmcs.begin(&myserial,9600);     //Uncomment if using software serial port. Comment this line if using hardware serial.
   rmcs.WRITE_PARAMETER(slave_id,INP_CONTROL_MODE,PP_gain,PI_gain,VF_gain,LPR,acceleration,speed);    //Uncomment to write parameters to drive. Comment to ignore.
   rmcs.READ_PARAMETER(slave_id);
   
}

void loop(void)
{
   Serial.print("Sending speed command (RPM):");
   Serial.println(speed_rpm);
   rmcs.Speed(slave_id,speed);                   //Set speed within range of 0-65535 or 0-(maximum speed of base motor)
   rmcs.Enable_Digital_Mode(slave_id,0);        //To enable motor in digital speed control mode. 0-fwd,1-reverse direction. 
   
//   delay(3000);
   Current_Speed=rmcs.Speed_Feedback(slave_id); 
   Serial.print("Current Speed feedback (RPM): ");
   Serial.println(Current_Speed/LPR+0.0);

//   delay(5000);
//   Serial.println("Break Motor");
//   rmcs.Brake_Motor(slave_id,0);                 //Brake motor. 0-fwd,1-reverse direction. 
//
//   delay(2000);
//   Serial.println("Changing direction");
//   rmcs.Enable_Digital_Mode(slave_id,1);           //To enable motor in digital speed control mode. 0-fwd,1-reverse direction. 

//   delay(3000);
//   Current_Speed=rmcs.Speed_Feedback(slave_id); 
//   Serial.print("Current Speed feedback : ");
//   Serial.println(Current_Speed);

   
//   delay(3000);
//   Serial.println("Disable Motor");
//   rmcs.Disable_Digital_Mode(slave_id,1);        //Disable motor in digital speed control mode. 0-fwd,1-reverse direction. 
//   delay(3000);
}

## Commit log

2020-04-22 py code refactoring
    [data.csv, data_best.csv, length_iterations.csv, oneP_best.csv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]
2020-05-24 arduino codes
2020-05-25 scripts for rpi
    [sensor_data.csv]
2020-05-30 rpi image post final test
    [sensor_data.csv, yad_data.csv]
